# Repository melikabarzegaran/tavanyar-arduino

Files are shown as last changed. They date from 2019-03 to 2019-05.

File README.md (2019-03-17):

# Tavanyar (Arduino)

Tavanyar is a system which detects and evaluates physical therapy exercises automatically using motion
tracking devices. This project consists of two parts: a piece of hardware and some kind of user interface.
This code is the hardware-side of the project.
 
## Diagram
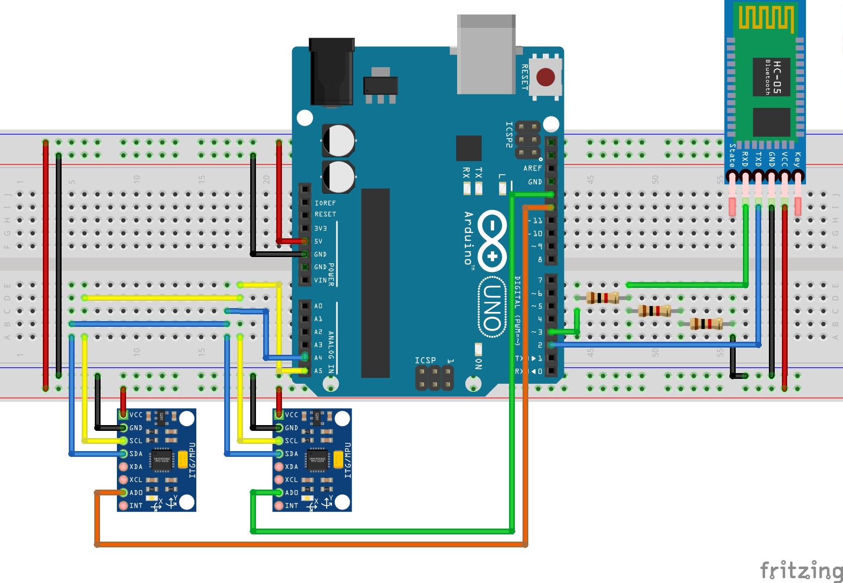
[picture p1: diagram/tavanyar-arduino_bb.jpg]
diagram


## Data flow
Two-way communication between hardware and user interface is made possible via bluetooth device:

1. Hardware -> User interface:

    Hardware can send 25 samples per second to the user interface. Each sample consists of the acceleration
towards x, y, and z axes of each device obtained by accelerometers, and the angular velocity around
x, y, and z axes of each device obtained by gyroscopes.

2. User interface -> Hardware:

    User interface can send commands to the hardware and configure the system. It can pause and resume
sending data, and also specify the number of motion tracking devices being used.

## Specifications
The hardware consists of:

1. One Arduino Uno as micro-controller
2. Multiple (currently 2) MPU-6050 modules as motion tracking devices
3. One HC-05 module as bluetooth device

### Arduino Uno specifications

- Clock frequency: the standard mode (100 KHz)
- Uses software serial protocol for debugging
- UART serial protocol standard: 8N1
- UART serial protocol baud rate: 38400 bps

### MPU-6050 specifications
- Accelerometer:
    - Full-scale range: +/-8 g
    - Sensitivity: 4096 LSB/g
    - Low pass filter:
        - Frequency: 5 Hz
        - Delay: 19 ms
    - Output rate: 1 KHz
- Gyroscope:
    - Full-scale range: +/-1000 dps
    - Sensitivity: 32.8 LSB/dps
    - Low pass filter:
        - Frequency: 5 Hz
        - Delay: 18.6 ms
    - Output rate: 1 KHz
- Sampling:
    - Frequency: 25 Hz
    - Divider: 39
- Clock reference: x axis of gyroscope
- Current consumption: 3.8 mA
- Uses digital input/output pins D13-D4 as address pins
- Uses 0x68 I2C address for the module under communication and 0x69 I2C address for other modules

### HC-05 specifications
- Name: TAVANYAR
- Password: 123456
- Uses software serial protocol for communication
- UART serial protocol standard: 8N1
- UART serial protocol baud rate: 38400 bps
- role: slave

### Note 1.
It is assumed that MPU-6050 modules are calibrated, and the corresponding calibration offsets are fed into the
system as well, all before running the sketch.

See this link in order to calibrate MPU-6050 modules and obtain calibration offsets:
https://github.com/melikabarzegaran/mpu6050-raw-calibration

### Note 2.
It is assumed that HC-05 module is configured before running the sketch.

See this link in order to configure HC-05 module:
https://github.com/melikabarzegaran/hc05-configuration

### Note 3.
We use 2 MPU-6050 modules with ASCII output format in the system, for the sake of simplicity and easy
debugging. For such a system, according to the table below, 38400 bps would be enough as serial baud rate.
Consider raising serial baud rate or shifting to binary output format when using more than 3 MPU-6050 modules.

|                      | 9600 bps | 19200 bps | 38400 bps | 57600 bps | 74880 bps | 115200 bps |
|:--------------------:|:--------:|:---------:|:---------:|:---------:|:---------:|:----------:|
| binary output format |     1    |     3     |     6     |     9     |     12    |     19     |
|  ASCII output format |     -    |     1     |     3     |     4     |     6     |      9     |

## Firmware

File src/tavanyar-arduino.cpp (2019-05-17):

/*
 * MIT License
 *
 * Copyright 2019 Melika Barzegaran <melika.barzegaran.hosseini@gmail.com>
 *
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
 * THE SOFTWARE IS PROVIDED "AS IS", WITHOUT WARRANTY OF ANY KIND, EXPRESS OR IMPLIED, INCLUDING BUT NOT LIMITED TO
 * THE WARRANTIES OF MERCHANTABILITY, FITNESS FOR A PARTICULAR PURPOSE AND NONINFRINGEMENT. IN NO EVENT SHALL THE
 * AUTHORS OR COPYRIGHT HOLDERS BE LIABLE FOR ANY CLAIM, DAMAGES OR OTHER LIABILITY, WHETHER IN AN ACTION OF
 * CONTRACT, TORT OR OTHERWISE, ARISING FROM, OUT OF OR IN CONNECTION WITH THE SOFTWARE OR THE USE OR OTHER DEALINGS
 * IN THE SOFTWARE.
 */

/*
 * title:
 *      Tavanyar (Arduino)
 *
 * description:
 *      Tavanyar is a system which detects and evaluates physical therapy exercises automatically using motion
 *      tracking devices. This project consists of two parts: a piece of hardware and some kind of user interface.
 *      This code is the hardware-side of the project.
 *
 *      Two-way communication between hardware and user interface is made possible via bluetooth device:
 *
 *          1. Hardware -> User interface:
 *          Hardware can send 25 samples per second to the user interface. Each sample consists of the acceleration
 *          towards x, y, and z axes of each device obtained by accelerometers, and the angular velocity around
 *          x, y, and z axes of each device obtained by gyroscopes.
 *
 *          2. User interface -> Hardware:
 *          User interface can send commands to the hardware and configure the system. It can pause and resume
 *          sending data, and also specify the number of motion tracking devices being used.
 *
 *      The hardware consists of:
 *          1. One Arduino Uno as micro-controller
 *          2. Multiple (currently 2) MPU-6050 modules as motion tracking devices
 *          3. One HC-05 module as bluetooth device
 *
 *      Arduino Uno specifications:
 *          - Clock frequency: the standard mode (100 KHz)
 *          - Uses software serial protocol for debugging
 *          - UART serial protocol standard: 8N1
 *          - UART serial protocol baud rate: 38400 bps
 *
 *      MPU-6050 specifications:
 *          - Accelerometer:
 *              - Full-scale range: +/-8 g
 *              - Sensitivity: 4096 LSB/g
 *              - Low pass filter:
 *                  - Frequency: 5 Hz
 *                  - Delay: 19 ms
 *              - Output rate: 1 KHz
 *          - Gyroscope:
 *              - Full-scale range: +/-1000 dps
 *              - Sensitivity: 32.8 LSB/dps
 *              - Low pass filter:
 *                  - Frequency: 5 Hz
 *                  - Delay: 18.6 ms
 *              - Output rate: 1 KHz
 *          - Sampling:
 *              - Frequency: 25 Hz
 *              - Divider: 39
 *          - Clock reference: x axis of gyroscope
 *          - Current consumption: 3.8 mA
 *          - Uses digital input/output pins D13-D4 as address pins
 *          - Uses 0x68 I2C address for the module under communication and 0x69 I2C address for other modules
 *
 *      HC-05 specifications:
 *          - Name: TAVANYAR
 *          - Password: 123456
 *          - Uses software serial protocol for communication
 *          - UART serial protocol standard: 8N1
 *          - UART serial protocol baud rate: 38400 bps
 *          - role: slave
 *
 *      Note 1.
 *      It is assumed that MPU-6050 modules are calibrated, and the corresponding calibration offsets are fed into the
 *      system as well, all before running the sketch.
 *
 *      See this link in order to calibrate MPU-6050 modules and obtain calibration offsets:
 *      https://github.com/melikabarzegaran/mpu6050-raw-calibration
 *
 *      Note 2.
 *      It is assumed that HC-05 module is configured before running the sketch.
 *
 *      See this link in order to configure HC-05 module:
 *      https://github.com/melikabarzegaran/hc05-configuration
 *
 *      Note 3.
 *      We use 2 MPU-6050 modules with ASCII output format in the system, for the sake of simplicity and easy
 *      debugging. For such a system, according to the table below, 38400 bps would be enough as serial baud rate.
 *      Consider raising serial baud rate or shifting to binary output format when using more than 3 MPU-6050 modules.
 *
 *      +----------------------+----------+-----------+-----------+-----------+-----------+------------+
 *      |                      | 9600 bps | 19200 bps | 38400 bps | 57600 bps | 74880 bps | 115200 bps |
 *      +----------------------+----------+-----------+-----------+-----------+-----------+------------+
 *      | binary output format |     1    |     3     |     6     |     9     |     12    |     19     |
 *      +----------------------+----------+-----------+-----------+-----------+-----------+------------+
 *      |  ASCII output format |     -    |     1     |     3     |     4     |     6     |      9     |
 *      +----------------------+----------+-----------+-----------+-----------+-----------+------------+
 *
 * configuration:
 *      +-----------------------+--------------------------------------------------+
 *      | Arduino Uno board pin | GY-521 break-out board #n pin (n=1,2,...,10) (*) |
 *      +-----------------------+--------------------------------------------------+
 *      |          VCC          |                        VCC                       |
 *      +-----------------------+--------------------------------------------------+
 *      |          GND          |                        GND                       |
 *      +-----------------------+--------------------------------------------------+
 *      |           A5          |                        SCL                       |
 *      +-----------------------+--------------------------------------------------+
 *      |           A4          |                        SDA                       |
 *      +-----------------------+--------------------------------------------------+
 *      |          AD0          |                     D(13-n+1)                    |
 *      +-----------------------+--------------------------------------------------+
 *      (*) In order to support more than 3 MPU-6050 modules, we should either raise the baud rate or shift to use
 *      binary output format instead of ASCII output format. `10` is just the number of free digital input/output
 *      pins of Arduino Uno, which are ready to connect to MPU6050 modules as address pins.
 *
 *      +-----------------------+----------------------------+
 *      | Arduino Uno board pin | ZS-040 break-out board pin |
 *      +-----------------------+----------------------------+
 *      |          VCC          |             VCC            |
 *      +-----------------------+----------------------------+
 *      |          GND          |             GND            |
 *      +-----------------------+----------------------------+
 *      |           D2          |           TXD (*)          |
 *      +-----------------------+----------------------------+
 *      |           D3          |          RXD (**)          |
 *      +-----------------------+----------------------------+
 *      (*) This connection is made directly.
 *      (**) This connection is made via voltage divider.
 *
 * author:
 *      Melika Barzegaran <melika.barzegaran.hosseini@gmail.com>
 *
 * version:
 *      1.0.0
 */

/*
 * Add MPU-6050 library, written by Jeff Rowberg <jeff@rowberg.net>.
 * Link to the library: https://github.com/jrowberg/i2cdevlib/tree/master/Arduino/MPU6050
 *
 * MPU-6050 library uses I2C serial protocol library, also written by Jeff Rowberg.
 * Link to the library: https://github.com/jrowberg/i2cdevlib/tree/master/Arduino/I2Cdev
 *
 * I2C serial protocol library uses the official Arduino I2C serial protocol library.
 * Link to the library: https://www.arduino.cc/en/reference/wire
 *
 * There is no need to add the lines below. They are added automatically by adding MPU-6050 library.
 * ```
 *      #include "I2Cdev.h"
 *      #include "Wire.h"
 *      #include "Arduino.h"
 * ```
 *
 * This library is used for the communication between Arduino Uno and MPU-6050 modules.
 */
#include "MPU6050.h"

/*
 * Add the official Arduino software UART serial library.
 * Link to the library: https://www.arduino.cc/en/Reference/SoftwareSerial
 *
 * This library is used for the communication between Arduino Uno and HC-05 module while allowing the board to be
 * programmed and debugged simultaneously.
 */
#include "SoftwareSerial.h"

/*
 * Define object for under-communication MPU-6050 module (MPU-6050 module which we are talking to).
 *
 * Used to transfer data between Arduino Uno and selected MPU-6050 module via I2C serial protocol.
 *
 * Input parameter is the address for MPU-6050 module we want to talk to in I2C serial protocol.
 *
 * When communicating with a MPU-6050 module:
 *      1. Set address pin of that module to low.
 *      2. Set address pins of other modules to high.
 *
 * +-------------------+---------------------------------+
 * | address pin (AD0) |   I2C serial protocol address   |
 * +-------------------+---------------------------------+
 * |  connected to GND |  0x68 (MPU6050_ADDRESS_AD0_LOW) |
 * +-------------------+---------------------------------+
 * |  connected to VCC | 0x69 (MPU6050_ADDRESS_AD0_HIGH) |
 * +-------------------+---------------------------------+
 */
MPU6050 selectedMotionTrackingDevice(MPU6050_ADDRESS_AD0_LOW);

/*
 * Total number of MPU-6050 modules in the system.
 * TODO: Update this when adding/removing a MPU-6050 module to/from the system.
 */
const int numberOfMotionTrackingDevices = 2;

/*
 * The array of address pins of MPU-6050 modules in the system.
 * TODO: Update this when adding/removing a MPU-6050 module to/from the system.
 */
const uint8_t addressPinArray[numberOfMotionTrackingDevices] = {13, 12};

/*
 * The struct for data read from sensors of a MPU-6050 module in a moment.
 */
struct Data {
    int16_t accelerometerX;
    int16_t accelerometerY;
    int16_t accelerometerZ;
    int16_t gyroscopeX;
    int16_t gyroscopeY;
    int16_t gyroscopeZ;
};

/*
 * The array of data read from sensors of MPU-6050 modules in the system.
 */
Data dataArray[numberOfMotionTrackingDevices] = {0};

/*
 * The struct for calibration offsets of a MPU-6050 module.
 */
struct CalibrationData {
    const int16_t accelerometerX;
    const int16_t accelerometerY;
    const int16_t accelerometerZ;
    const int16_t gyroscopeX;
    const int16_t gyroscopeY;
    const int16_t gyroscopeZ;
};

/*
 * The array of calibration offsets of MPU-6050 modules in the system.
 * TODO: Update this when adding/removing a MPU-6050 module to/from the system.
 */
const CalibrationData calibrationDataArray[numberOfMotionTrackingDevices] = {
        {-3338, 1077, 1184, 71, -13, 121}, /* 2, 0, 16382, 0, -1, -1 */
        {-1900, -44,  1243, 46, 61,  34} /* 6, 5, 16386, 0, 0, 1 */
};

/*
 * Pin chosen as receive pin of Arduino Uno in software UART serial protocol.
 * It should be connected to the TXD pin of HC-05 module, directly.
 */
const int rxdPin = 2;

/*
 * Pin chosen as transfer pin of Arduino Uno in software UART serial protocol.
 * It should be connected to the RXD pin of HC-05 module, via voltage divider.
 */
const int txdPin = 3;

/*
 * Define object for HC-05 module.
 *
 * Used to transfer data between Arduino Uno and HC-05 module via software UART serial protocol.
 *
 * Input parameters are, respectively, receive and transfer pins of Arduino Uno in UART serial protocol.
 */
SoftwareSerial bluetoothDevice(rxdPin, txdPin);

/*
 * Receiving this command means to pause sending data over bluetooth.
 */
const int pauseCommand = 0;

/*
 * Receiving this command means to resume sending data over bluetooth.
 */
const int resumeCommand = 1;

/*
 * Receiving this command means that we should use the first MPU-6050 module while sending data over bluetooth.
 */
const int use1MotionTrackingDeviceCommand = 2;
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

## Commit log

2019-03-16 feat: Add tavanyar-arduino.cpp file
2019-03-17 docs: Add breadboard diagram with fritzing
    [tavanyar-arduino.fzz]
2019-05-17 feat: Update calibration data
